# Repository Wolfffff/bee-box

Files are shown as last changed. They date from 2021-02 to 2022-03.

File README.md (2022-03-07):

# Tracking Bumblebee Social Networks

## Analysis
Folder containg both R and Python analysis code for analyzing imaging data...

python /Genomics/ayroleslab2/scott/bees/bee-box/analysis/aruco_tools/matching_pipeline.py /Genomics/ayroleslab2/scott/bees/new_training/20210909_run000_00000000_48Hrs_libx264_1h.mp4 /Genomics/ayroleslab2/scott/bees/new_training/predictions/output_2022-02-01.slp /Genomics/ayroleslab2/scott/bees/new_training/test pipeline_test 0 1200 -a -p -v 1

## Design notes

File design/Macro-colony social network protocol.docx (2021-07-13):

Materials: (Blue materials on Github)

Macrocolony:

1x BeeGo Base (27x27 cm)

1x BeeGo Roof (27x27 cm)

8x BeeGo Straight Brick (7.5 cm)

4x BeeGo Straight Brick (4.5 cm)

4x BeeGo Corner Brick

4x BeeGo “Tacks”

1x BeeGo Wax Catcher

1x Reservoir

¼ lb Soy Wax

Aluminum Foil

9x Wicks

Microcolony:

1x Partitioned Microcolony (14 x 14 cm)

4x BeeGo “Tacks”

1x Partitioned Roof (14x14 cm)

1x Reservoir

1x KimWipe

1x Wick

10 mL 40% Sucrose Solution/4 bees

1 Gnocchi-sized ball of Pollen Dough (doughy mix of ground pollen & honey)/4 bees

1 Penny-sized ball of wax/4 bees

1 4x4 ARUCO Tag/Bee (printed using Silhouette and Cameo)

2 IR Light Chandeliers (requires 7 IR lights each)

6 Infrared Lights

1 Falcon Tube/3 Bees

1 Ice Bucket (with ice...duh)

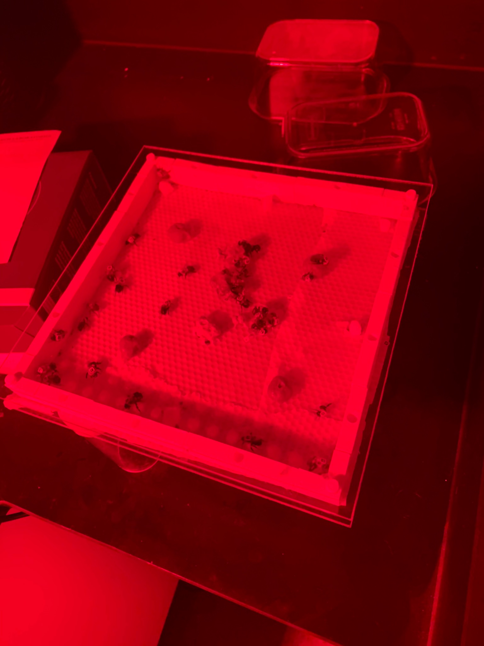
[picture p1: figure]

1a. Assemble the Macrocolony

  a. Take one BeeGo Base, and cover all holes with aluminum foil
  b. Insert BeeGo Blocks in the above pattern (25.5 cm x 25.5 cm). Puncture the aluminum foil with the blocks (it helps to flatten the foil with your hands very lightly before inserting the blocks). Tape the connections between the block and aluminum foil to prevent the wax from leaking.
  c. Cover the aluminum foil with the “wax-catcher” so it is flush with one corner of the base. There should be approximately a 5x5 cm region on the opposite corner which isn’t covered by the acrylic wax catcher.
  d. Melt soy wax and fill the colony 2 mm thick with melted soy wax. Let solidify.
    i. Note: beeswax will disrupt the chemical communication in the hive. Avoid using it.
  e. Replace the two 7.5 cm BeeBlocks with a vented Bee Block
    i. Note: wax will melt through those blocks if you don’t add them beforehand!
  f. Use “tacks” to attach acrylic roof of the macrocolony.
  g. Fill the reservoir up to 3 mm thick with 40% sucrose solution
  h. Use a razor to cut the uncovered 5x5 cm corner out. Use the smallest lego piece to puncture 9 holes in that corner. Fill those holes with wicks, and place over the reservoir. Put over another reservoir on the other corner as a balance.
  i. Add wax & pollen dough to the center of the colony.

1b. Assemble the Microcolony

a. Take one microcolony
b. Cover the microcolony with a kimwipe. Add wax & pollen dough kitty corner to the hole
c. Fill the reservoir up to 3 mm thick with 40% sucrose solution
d. Fill hole with a wick, and connect to macrocolony.
1. Tagging bees

Note: for every step here, do under red light. Bees struggle ti see red light, and it will make the ordeal less stressful for them. For long term imaging, try to use infrared light instead.

a. Obtain untagged bees in test tubes (1-4 bees per tube)
  i. To get individual bees, remove three of the four “tacks” and slide the lid to expose one corner. Slide a piece of paper between the plexiglass top and walls of the corner diagonal from the remaining tack. This will ensure only one section of the base is open for bees to escape.
  ii. Using a Falcon tube, capture individual bee. Place the tube next to or over the target bee. Once a bee has moved into the tube, pick up, place the lid and close carefully. Slide the base closed carefully ensuring no bees have escaped or have climbed the walls
  iii. Note: You can put multiple bees in the same falcon tube, but it’s easier when the other bees are chilled.
b. Chill bees in test tubes on ice for about 15 minutes or until immobile
  i. Note: cover falcon tubes completely with ice.
c. Take one test tube and place immobile bees wings-up on solid surface
d. Using insect pins, dab a small amount of super glue on each bee’s back between head and wings
e. Using another insect pin, stab tag and place carefully on bee’s back where glue was placed.
  i. Note: here it is helpful to have three pins. One for super glue, one for the tag and a third to help you maneuver and press down your tag. After using the upright pin to place the tag onto the super glue, using the long side of the third pin press the tag down into the super glue to make sure it’s properly adhered.
  ii. Note: Make sure to orient the tag so that the dot is facing forward from the bees perspective.
f. Once all bees are tagged, allow to rest on ice for a few minutes to allow glue to set.
  i. Note: Be careful that the bees cannot get wet!
g. Put bees back in BeeGo Base with their bellies down to make sure that excess glue does not stick to the base.
h. Wait for bees to wake up (a few minutes) to ensure tags remain and no individual bee is stuck to walls or base.
2. Colony Maintenance:
  a. Bees should have continuous access to bee bread and 40% sucrose solution
  b. Bee Bread: made in bulk. A mixture of raw honey and bee pollen to form a dough-like consistency. Small ball units of bee bread are frozen to kept fresh and can be placed directly into macrocolony when needed.
  c. Sucrose Solution:
    i. Mix 40 grams of sugar with 60 grams of water in a Falcon tube & shake until sugar is completely dissolved
    ii. Fill reservoir with the sucrose solution.
  d. Every day, replace vials of sugar water and check quantity of pollen and wax.
3. Filming
  a. We will be filming on the 5th and 7th day of the microcolony, and on the 1st through 5th days of the macrocolonies.
    i. The rationale behind this is that microcolonies need time for a dominance hierarchy to develop (Amsalem et. al) while our macrocolonies should have a pre-existing colony.
  b. On the day of filming, move bees to film studio at 10:00 am.
    i. Do this in their respective containers.
    ii. Note: Timing matters here! Bees, like humans, have strong circadian rhythms -- we do not want a batch effect because some bees are being filmed bright and early while others are being filmed late.
  c. Put macros on top of heating pad, and micros on top of a small tarp to catch sugar water (shouldn’t be necessary with new reservoirs)
  d. Adjust settings
    i. General parameters: FR: 20 frames/s, Exposure: 10000 us, Gain: 5 dB
  e. Begin filming for 24 hours on labcams.
  f. At 11:00 am, remove colony.
    i. If doing RNA-seq, move each bee to an eppendorf, label the tube with the tag number and eclosion date, and flash freeze the bees in dry ice. Put the frozen bee in the appropriate box of the -80 freezer.
    ii. Otherwise, put in the hallway -80 freezer for 24-48 hours, then throw out the bees.
    iii. Note: If you need to both film & remove a colony, try to use the one hour flex time to transfer between the two. If space is a concern, you can remove the old colony a few minutes early and it won’t be a huge problem.

Current Goals:

Main Researchers | Question | Current Materials Using Above Protocol
Tatum’s Project | Influence & Aggression in Microcolonies | 4 Microcolonies (all from ST)
Alexis’ Project | Titrating Aggession Into Microcolonies | 24 Microcolonies: 8 with no JH bees, 8 with 1 JH bee, 8 with 2 JH bees (all from ST)
Dee’s Project | Developing a Social Network of Macrocolonies | 3 Macrocolonies: 2 older ones (from HP), one newer one (from ST)

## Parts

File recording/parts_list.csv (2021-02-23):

Name | Manufacturer | Part Number | URL | Description
daier 20 Sets Mini Micro Jst 2.0 Ph 2-Pin Connector Plug Male with 150mm Cable & Female | daier | B01DUC1O68 | https://www.amazon.com/daier-Micro-2-Pin-Connector-Female/dp/B01DUC1O68
AimHD 20 Pack Female Power Pigtail DC 5.5mm x 2.1mm Connectors Upgraded AWG for CCTV Surveillance Security Camera System and Led Strips Transformer Connection | AimHD | AHD-DC20-F-PT | https://www.amazon.com/Connectors-Upgraded-Surveillance-Transformer-Connection/dp/B0768V9V5Q
12V 2A Power Supply AC Adapter, AC 100-240V to DC 12 Volt Transformers, 2.1mm X 5.5mm Wall Plug (12 Volt - 2amp - 2pack) |  | B077PW5JC3 | https://www.amazon.com/100-240V-Transformers-Switching-Applications-Connectors/dp/B077PW5JC3

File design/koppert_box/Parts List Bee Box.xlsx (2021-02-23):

Bee Box Hardware (not printed) | Price | # per unit | Total price per unit | Link | Notes | # Ordered Dec 6 |  | recieved?
Raspberry Pi 4 Model B 8GB RAM w/ power supply | 89.95 | 1 | 89.95 | https://www.canakit.com/raspberry-pi-4-basic-kit.html | unit comes w/ power suply and heat sinks | 5 |  | y
32 GB SD card for the Pi | 8.98 | 1 | 8.98 | https://www.amazon.com/SanDisk-Ultra-microSDXC-Memory-Adapter/dp/B073JWXGNT?hvadid=309776868400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 |  | 5 |  | y
Raspberry Pi High Quality Camera | 50 | 1 | 50 |  |  | 5
15-pin Flexible Flat Cable (FFC), 30cm | 1.9 | 1 | 1.9 | https://www.dfrobot.com/product-2035.html |  | 6 | Ordered this alternative: https://www.amazon.com/Raspberry-Extension-Flexible-Connection-Navigation/dp/B07KSRQYMZ | y
Arducam 12mm Lens | 49.99 | 1 | 49.99 | https://www.amazon.com/Arducam-Varifocal-C-Mount-Raspberry-Adapter/dp/B088GT6N3Z?th=1 |  | 5 |  | y
Spotlights | 25 | 6 | 150 | https://www.amazon.com/uxcell-Infrared-Degree-Illuminator-Security/dp/B07PYX9F59?s=electronics | Alternate?: https://www.amazon.com/uxcell-Infrared-Degree-Illuminator-Security/dp/B07PZWJ6ZC?s=electronics | 15 2 packs |  | ~
12V power adapter | 11.99 | 1 | 11.99 | https://www.amazon.com/100-240V-Transformers-Switching-Applications-Connectors/dp/B077PW5JC3?s=electronics | Confirm w/ August, alternative: https://www.amazon.com/Chanzon-Switching-Adapter-100-240V-Transformer/dp/B07HNV6SBJ?s=electronics | 5 x 20 pack |  | y
JST jumper wire | 6 | 6 | 36 | https://www.sparkfun.com/products/9914?_ga=2.118607497.1221790544.1603221893-371982142.1603221893 | Confirm # with August, alternate source: https://www.amazon.com/daier-Micro-2-Pin-Connector-Female/dp/B01DUC1O68 | 5 x 20 pack from alternate source |  | y
Female DC Power Cable | 1 | 1 | 1 | https://www.cableleader.com/1ft-dc-power-cable-pigtail-female-plug.html | Alternative: https://www.amazon.com/Connectors-Upgraded-Surveillance-Transformer-Connection/dp/B0768V9V5Q | 3 x 20 pack | ordered from amazon source
Finish Nail for the inner bee door (1") | 0.5 | 1 | 0.5 | https://www.mcmaster.com/97828A670/ | confirm length and # w/ August | 1 x 1 lb box |  | y
 |  |  | 0
 |  |  | 0
Hinge Door Hardware |  |  | 0
broad hinges 3/4", 19mm Hillman Hardware Essentials, part # 851189 (2, there are 4 per pack) | 5.88 | 2 | 11.76 | https://www.hillmangroup.com/us/en/Home-Solutions/Builders%27-Hardware/Miniature/Hinges-Minature/Hardware-Essentials-Broad-Hinges/p/851189 | Confirm with August, alt source: https://www.amazon.com/Hillman-Group-851189-4-Inch-1-Inch/dp/B00EALUEJ2 | 6 x 2 pack (from amazon source) |  | y
4-40 x 1/2" screws | 0.25 | 8 | 2 | https://www.mcmaster.com/91251A110/ |  | 1 x 100 pack |  | y
4-40 nuts | 0.1 | 12 | 1.2 | https://www.mcmaster.com/90480A005/ |  | 3 x 100 pack |  | y
4-40 x 1" screws | 0.25 | 4 | 1 | https://www.mcmaster.com/90044A111/ |  | 4 x 25 pack |  | y
 |  |  | 0
Pi Camera Mount Hardware |  |  | 0
6-32 x 3/4" screws | 0.25 | 4 | 1 | https://www.mcmaster.com/91251A151/ |  | 2 x 100 pack |  | y
6-32 nuts | 0.1 | 4 | 0.4 | https://www.mcmaster.com/90480A007/ |  | 3 x 100 packs |  | y
 |  |  | 0
Raspberry Pi Mount Hardware |  |  | 0
2-56 x 3/8" screws | 0.25 | 4 | 1 | https://www.mcmaster.com/91251A079/ |  | 2 x 100 pack |  | y
2-56 nuts | 0.1 | 4 | 0.4 | https://www.mcmaster.com/90480A003/ |  | 3 x 100 pack |  | y
 |  | Total $ per unit | 419.07
 |  | # units | 50
 |  | Total equipment cost: | 20953.5

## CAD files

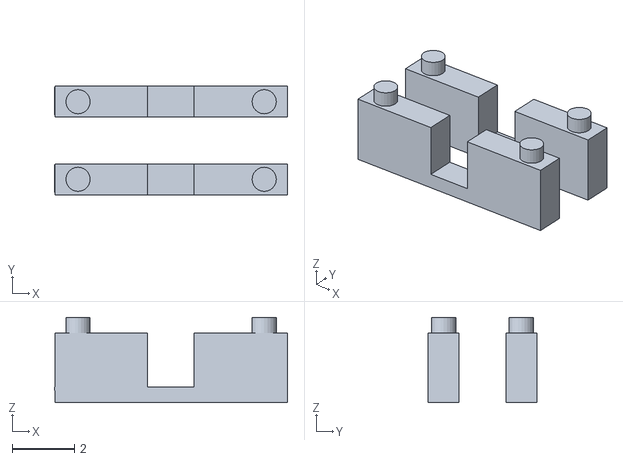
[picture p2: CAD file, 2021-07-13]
design/macro/VentedBeeGoBrick.stl
7.51 x 3.50 x 2.75

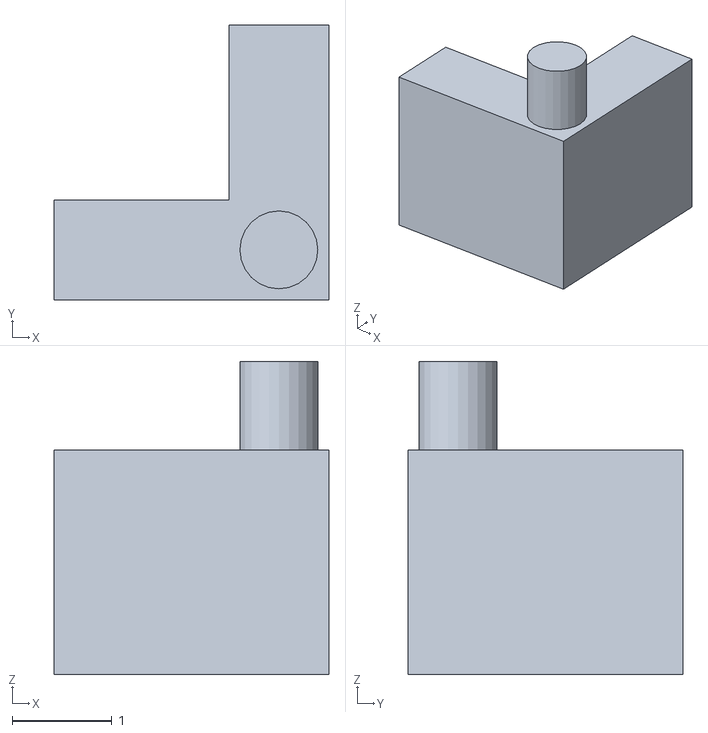
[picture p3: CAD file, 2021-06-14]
design/macro/BeeGoCorner_051621.stl
2.75 x 2.75 x 3.13

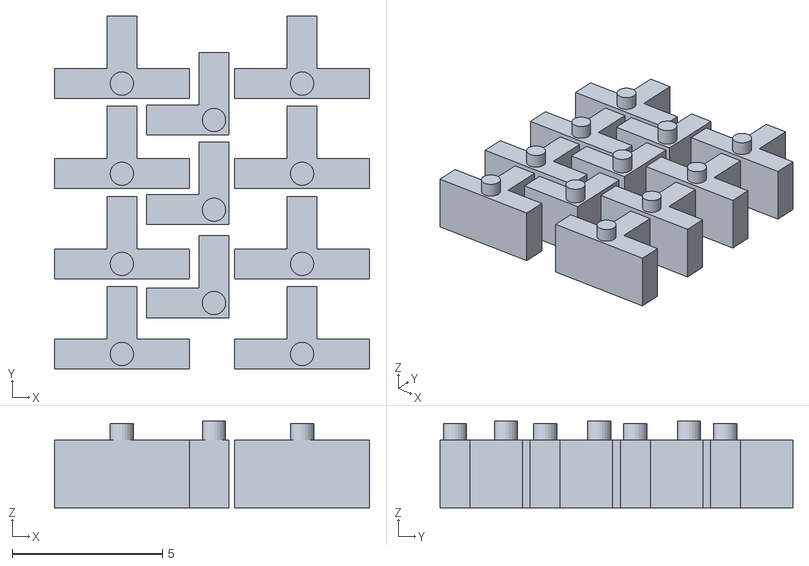
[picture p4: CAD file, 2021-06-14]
design/macro/TsAndLs.stl
10.5 x 11.7 x 2.88

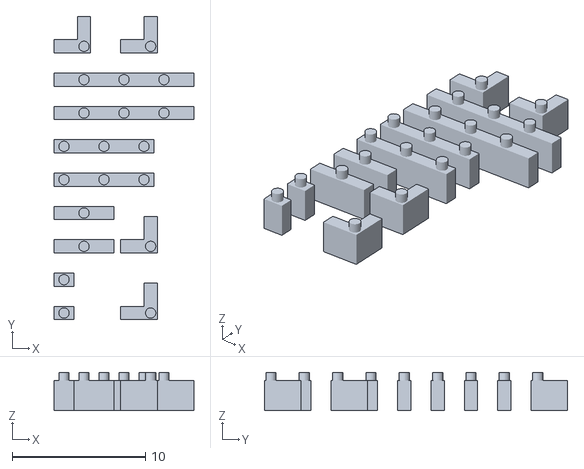
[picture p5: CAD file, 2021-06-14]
design/macro/BeeGoSmallerPieces_051721.stl
10.5 x 22.8 x 2.88

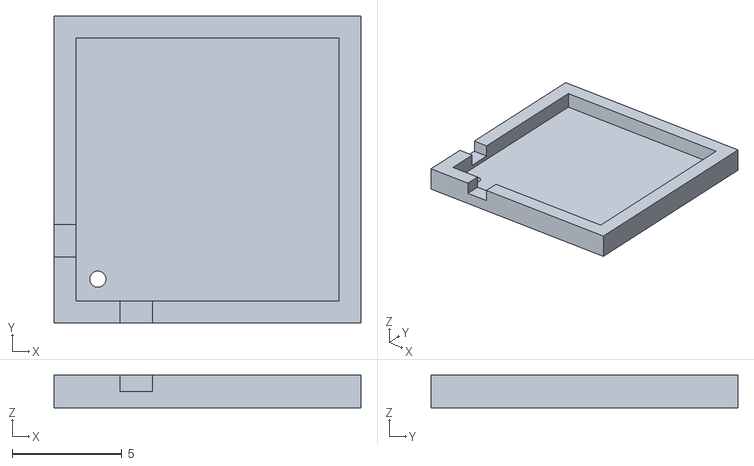
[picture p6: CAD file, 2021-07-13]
design/071221_VentedPartitionedMicro.stl
14.0 x 14.0 x 1.50

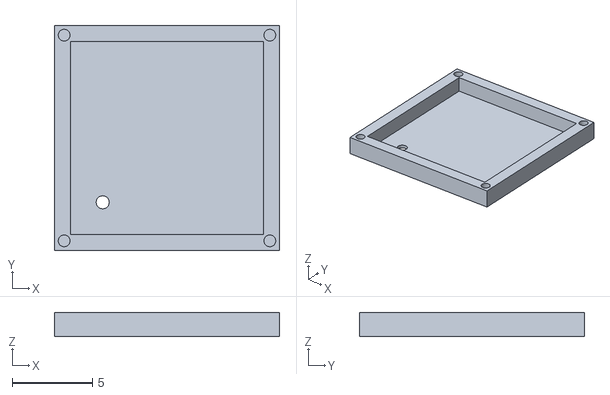
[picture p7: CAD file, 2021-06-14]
design/micro/04272021_SmallPartitionedArena.stl
14.0 x 14.0 x 1.50

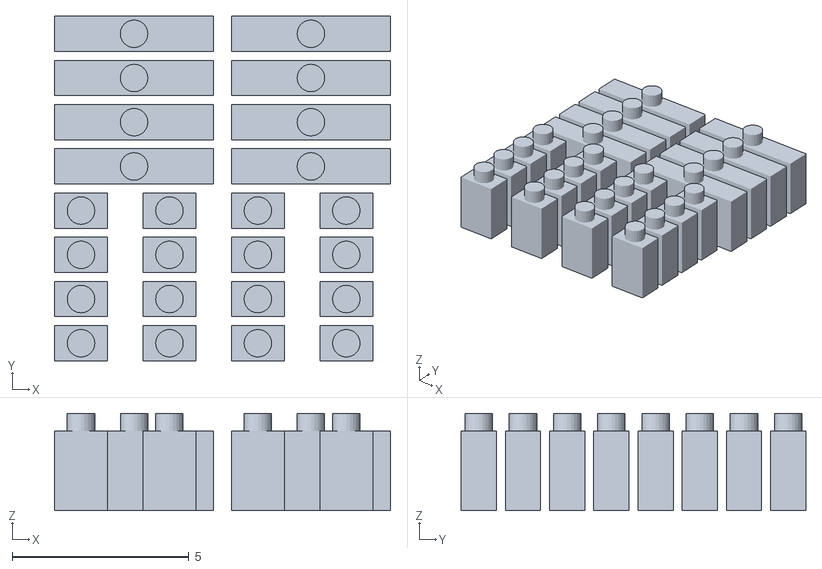
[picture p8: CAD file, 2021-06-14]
design/macro/202105_SmallSet1Unitand3UnitBeego.stl
9.50 x 9.75 x 2.75

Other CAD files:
design/macro/JustLongPieces_051821.dwg
design/koppert_box/202101_KoppertBox_Plug.dwg
design/070221_Reservoir.stl
design/koppert_box/202101_KoppertBox_RimInner.f3d

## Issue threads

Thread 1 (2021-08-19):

### ISSUE TITLE
Parallelization breaks frame numbering in output

### ISSUE THREAD

**Issue by Wolfffff** [Wolfffff/bee-box#1]
[matching_pipeline.py](https://github.com/Wolfffff/bee-box/tree/main/analysis/aruco_tools)

When using the -p flag, frame numbers are only returned for a small portion of the data frame(likely a chunk) with others returned as 0.

**Comment by dyknapp** [comment]
Fixed!  This was a bug arising from insertion of rows for missing tags into the partial results matrices retrieved from the processes.  Specifically, in some cases, the program would mistake the first row containing frame numbers as being in place of a missing row and consequently add a row filled with zeros.

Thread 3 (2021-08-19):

### ISSUE TITLE
Rolling window tag-track association slows down as size grows

### ISSUE THREAD

**Issue by Wolfffff** [Wolfffff/bee-box#3]
It appears that as we pus our data into the hundreds of tens of frames, the performance of the rolling window tag-track association drops drastically.  This could be due to the growing size of tags and tracks as our frame count grows.

**Comment by dyknapp** [comment]
Fixed!  All completely-zero rows and columns are removed _prior_ to Hungarian matching.  Previously, Hungarian matching was being applied on the full cost matrix that had a ton of meaningless columns and rows, before meaningless data was filtered out afterwards.  With the new prior removal method, we also lost the need for the filtering afterwards.

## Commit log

2021-02-22 Adding basic designs and recording.md
    [202101_KoppertBox_RimInner.f3d]
2021-02-23 Basic part_list(to be removed) + cleaning
    [parts_list.csv]
2021-02-23 Added Parts List
    [Parts List Bee Box.xlsx]
2021-06-13 Added A TON of Design Files
    [04272021_SmallPartitionedArena.stl, 202101_KoppertBox_Plug.dwg, BeeGoCorner_051621.stl, BeeGoSmallerPieces_051721.stl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]
2021-06-28 Revamp and cleaning
    [04272021_SmallPartitionedArena.stl, 202101_KoppertBox_Plug.dwg, 202105_SmallSet1Unitand3UnitBeego.stl, BeeGoCorner_051621.stl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]
2021-07-13 Added Protocol, Vented Tops/Sides, and Reservoir Drafts
    [070221_Reservoir.stl, 071221_VentedPartitionedMicro.stl, VentedBeeGoBrick.stl]
2021-07-14 Added Vented Holes
2021-07-20 New file for entire ArUco and SLEAP matching pipeline
    [20210706_run000_00000000_aruco_annotated_30p_threshold.csv, aruco_sleap_matching_output.csv, aruco_sleap_matching_output_merged.csv, cost_matrix.csv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]
2021-07-20 Deleted a bunch of meaningless files
    [20210706_run000_00000000_aruco_annotated_30p_threshold.csv, aruco_sleap_matching_output.csv, aruco_sleap_matching_output_merged.csv, cost_matrix.csv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]
2021-07-28 Commit to keep final changes before deleting superfluous files
    [aruco_sleap_matching_output.csv, test.csv]
2021-07-28 Reorganized /aruco_tools significantly. Refer to older commits for a lot of now-deleted files.
    [aruco_sleap_matching_output.csv, test.csv]
2021-07-28 Multiprocessing now working. Some (minor) bugs remain
    [test.csv]
2021-07-28 Minor bug fix
    [test.csv]
2021-07-28 Console output redirection, removed superfluous save of matching results
    [test.csv]
2021-08-20 Fixing writing to allow annotating from non-zero start frames.
2021-08-20 Fixing "write dump" first frame when starting from non-zero frame
2021-08-20 Adding threads arg, drawing box of crop size when annotating, and addition of scale factor for video writing
2021-10-19 Moving main branch R code to develop
    [mp_test_aruco_data_with_track_numbers.csv, mp_test_matching_result.csv]
2021-10-21 Log output changes
    [mp_test_aruco_data_with_track_numbers.csv, mp_test_matching_result.csv]
2022-02-08 Updating plotting and filters
